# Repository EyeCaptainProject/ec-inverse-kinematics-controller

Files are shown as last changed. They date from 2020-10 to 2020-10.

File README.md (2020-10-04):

# EyeCaptain Mechanical Joystick Controller

This controller can be used to control a joystick if there is no direct digital interface, e.g. to control a wheelchair joystick that has no R-NET or DX-BUS interface. It consists of a 3d-printed part and an Arduino NodeMCU. The mechanical adapter is just mounted on the top of the existing joystick.

## Disclaimer

EyeCaptain does not take any responsibility for the use of the codes and hardware suggestions published here. If you use parts of this project for your own use or for another project, you do so at your own risk. You must check for yourself whether it is a medical device and, if necessary, observe and comply with the guidelines for use and publication applicable in your country. 

# The joystick adapter


We designed a 3D printable mechanical adapter, which can be adjusted in order fit many different joysticks. Two arms are moved by servo motors, which are controlled by an NodeMCU (similar to Arduino Nano, but with WIFI module). The NodeMCU itself is connected to a tablet (via USB or WIFI) and receives the data for direction and speed.

The mechanical adapter consists of four parts:

- 3D printed adapter
- NodeMCU 
- two servo motors (e.g. D-Power DS3218 RC Servo)
- external power supply (necessary because of the quite heavy power consumption of the servo motors)

There are two different ways to connect the NodeMCU to the tablet:
- USB cable
- WIFI

## What is inverse kinematics?

The approach we used in the design is called "inverse kinematics". This means, that the calculation of the coordination at the end of an kinematic line is done backwards. So instead of calculatig the coordinates of the joystick base on the angles of the servo motors, the angles are calculated from the coordinates provided by the devices that delivers x/y positions

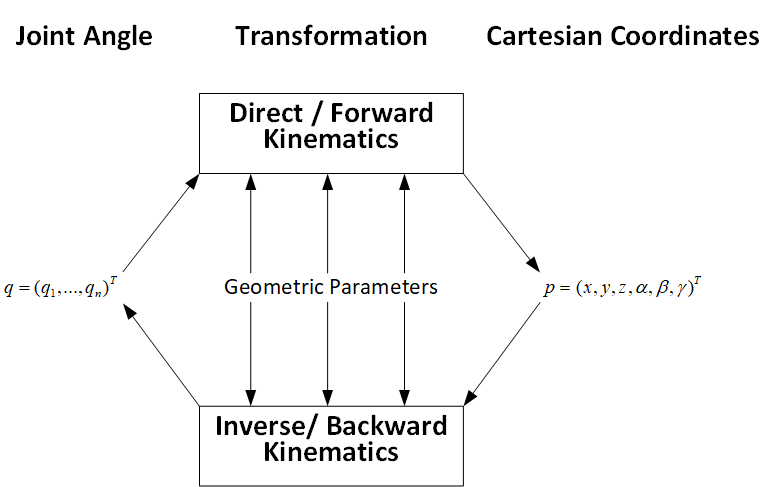
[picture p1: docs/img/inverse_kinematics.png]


The design resembles a 5 bar linkage as shown in the image below, but the horizontal bar a is replaced by the defined position of the servo motors. The two arms in our design consist of the parts "d", "e", "c" and "d", as shown in the image. The blue dot marks the joystick position from a top view and the angles theta1 and theta2 are the angles of the servo motors.

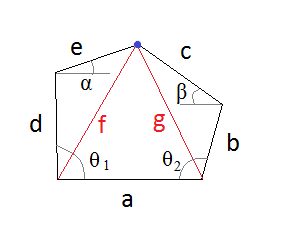
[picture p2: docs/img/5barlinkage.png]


## Steps to build this project

### 1) Print the files in the CAD_Models folder
If you don't have an own 3D printer you may ask the next maker space around you. Very often you find kind people there who are willing to help with printing some parts. 

If you have no idea where the next maker space ist located, you may have a look on this site: [makerspaces.make.co](https://makerspaces.make.co/).

### 2) Assemble all parts (see the images of the assembled model at the top for now, instructions will follow)

### 3) Wire the NodeMCU to the servos and the power supply

The Arduino and the servo motors are connected as depicted in the following image: 

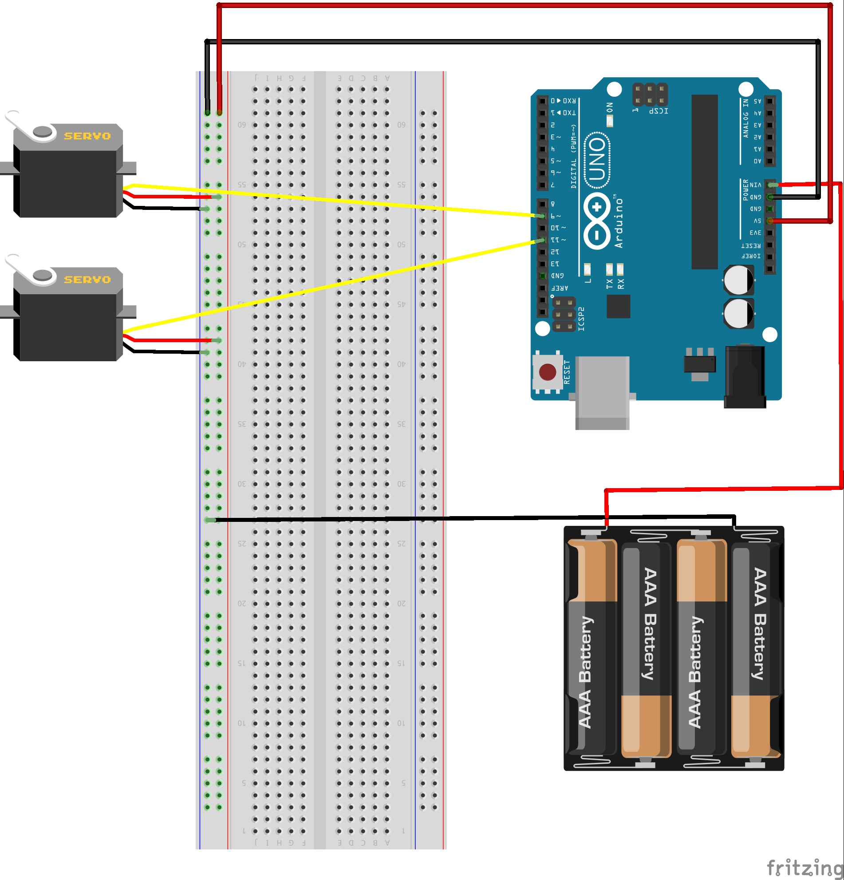
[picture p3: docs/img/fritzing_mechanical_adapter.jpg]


The image above only shows the schematics. For production use, we highly recommend to solder everything to a standard PCB instead of using a breadboard.

### 4) Configure and upload the arduino software to the NodeMCU

- Serial connection is set to `115200` bytes
- The Arduino/NodeMCU software receives X/Y-data (e.g. from a tablet or a phone) and controls the joystick movements with two servo motors and two arms.
- NodeMCU starts a Wifi Hotspot named `EyeCaptain` with the password `EyeCaptain`
- There is a websocket server running on the Ardino device.
- The current implementation of the Arduino-Code also has a webserver with a simple implementation for mobile phones (Folder: `Arduino/data/` that enables you to test the X/Y-position transmission. In order to upload it, you need to use the following Plugin for the Arduino IDE: https://github.com/esp8266/arduino-esp8266fs-plugin. All data that lies in the `Arduino/data` directory will be uploaded to the NodeMcu.
- Once the arduino is running, position data can be sent to either via Websocket-messages or via a Serial Port in the following structure:
```C
%<POSX>,<POSY>;
// e.g.Example:
%50,50;
```
- Position data is between -100/-100 (bottom left) and 100/100 (top right). 0/0 should be the center position
- Files and options that you should configure
    - `Arduino/InverseKinemetics.ino`:
        - Pin configuration
            - `SERVOPINLEFT`: pin of the left servo
            - `SERVOPINRIGHT`: pin of the right servo
        - Adjust the following factors until the servos move exactly 90 degrees
            - `SERVOFAKTORLEFT`: 
            - `SERVOFAKTORRIGHT`:
        - Adjust the NULL-values so that the servo arms are parallel at all times
            - `SERVOLEFTNULL`:  
            - `SERVORIGHTNULL`:
        - You might also need to change the following values:
            - `L1`, `L2`, `L3` (arm length)
            - `O1X`, `O1Y`, `O2X`, `O2Y` (origin point of left and right servo)
        - Parking positions if no data is comin in 
            - `PARKX`
            - `PARKY`        
    - `Arduino/data/websocket.js`: 
        - `IP_ADDRESS` must contain the IP address of the NodeMcU

### 5) Open your browser and connect to the NodeMCU via web iterface

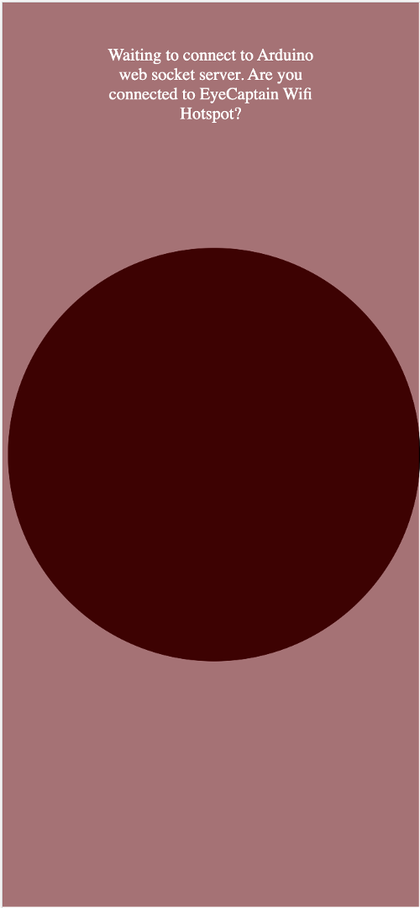
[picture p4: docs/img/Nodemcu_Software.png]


# Explanation of the arduino codes:

- The arduino code in this project is based on the following work of Johannes Heberlein (2014). 
    - https://github.com/9a/plotclock

### Libraries 

Libraries needed:

- https://github.com/Links2004/arduinoWebSockets

```c
#include <ESP8266WiFi.h>
#include <ESP8266WiFiMulti.h>
#include <ArduinoOTA.h>
#include <ESP8266WebServer.h>
#include <ESP8266mDNS.h>
#include <FS.h>
#include <WebSocketsServer.h>
#include <Servo.h>
```

### Calibration

Calibration of servo motor position. Because the lever of the motors are never at the exact same position, it is necessary to calibrate the motors prior to first use in the project.

```c
// Adjust the following factor until the servos move exactly 90 degrees
// D-POWER-servos: 
#define SERVOFAKTORLEFT 700
#define SERVOFAKTORRIGHT 460
// Zero-position of left and right servos
// When in calibration mode, adjust the NULL-values so that the servo arms are at all times parallel
// either to the X or Y axiste
// D-Power servos Werte:
#define SERVOLEFTNULL 2000
#define SERVORIGHTNULL 1050
```

### Geometry factors

The following code describs the geometry of the adapter, which is used for the calculation of the angels (inverse kinematics).

```c
// length of arms
#define L1 35
#define L2 45
#define L3 0 //13.2

// origin points of left and right servo 
#define O1X 40
#define O1Y -25
#define O2X 48
#define O2Y -25
```

### WIFI connection

The nodeMCU sets up an access point for the tablet to log in (WIFI). The name of the network and the passwort are defined in the code.

```c
ESP8266WiFiMulti wifiMulti;       // Create an instance of the ESP8266WiFiMulti class, called 'wifiMulti'

ESP8266WebServer server(80);       // Create a webserver object that listens for HTTP request on port 80
WebSocketsServer webSocket(81);    // create a websocket server on port 81

File fsUploadFile;                 // a File variable to temporarily store the received file

const char *ssid = "EyeCaptain"; // The name of the Wi-Fi network that will be created
const char *password = "EyeCaptain";   // The password required to connect to it, leave blank for an open network

const char *OTAName = "eyecaptain";           // A name and a password for the OTA service
const char *OTAPassword = "eyecaptain";

const char* mdnsName = "eyecaptain"; // Domain name for the mDNS responder
```

### Serial connection

If the NodeMCU is connected to the tablet via WIFI, the serial connection is only for debugging. But you can also use the serial connecting for transmitting the coordinates from the tablet to the Arduino.

```c
Serial.begin(115200);        // Start the Serial communication to send messages to the computer
```

# Overview of the mechanics 3d Parts:

#### Base_Plate.stl
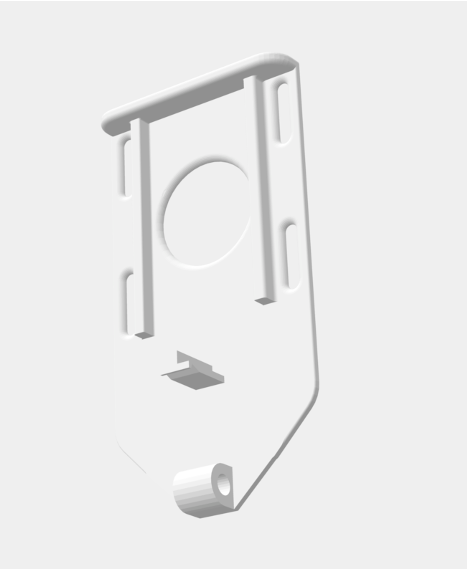
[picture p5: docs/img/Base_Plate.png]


#### Servo_Mount.stl: Holds the two servos
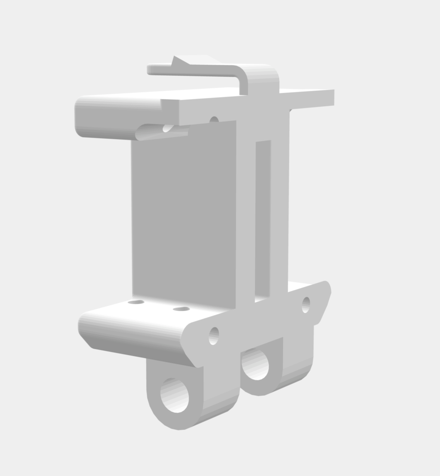
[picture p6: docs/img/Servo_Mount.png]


#### Arm_1.stl
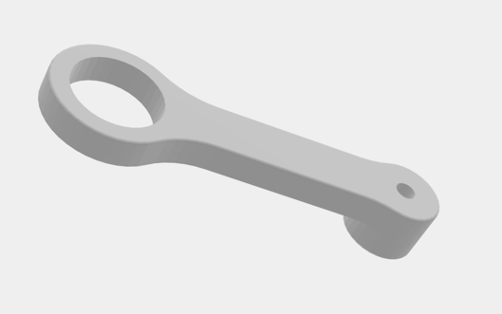
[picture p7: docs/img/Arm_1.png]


#### Arm_2.stl
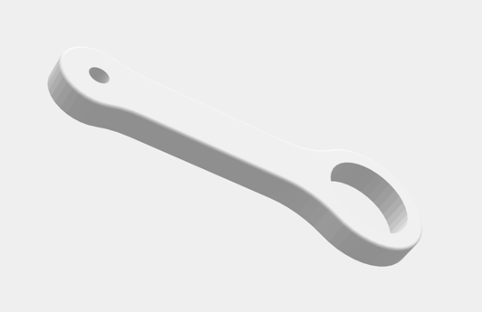
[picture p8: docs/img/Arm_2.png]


#### Arm_Mount_Part1.stl
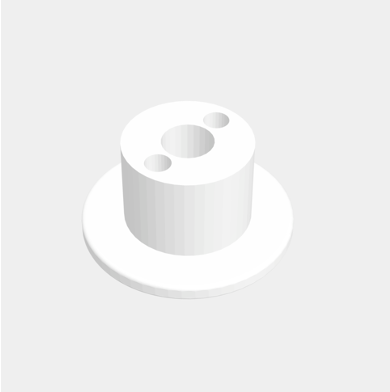
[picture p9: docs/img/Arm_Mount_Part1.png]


#### Arm_Mount_Part2.stl
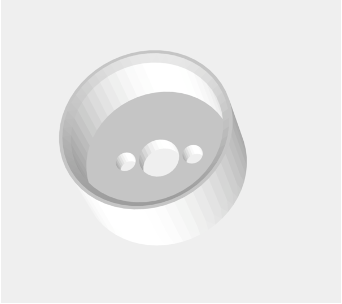
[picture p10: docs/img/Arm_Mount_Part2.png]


#### Simple_Stick.stl
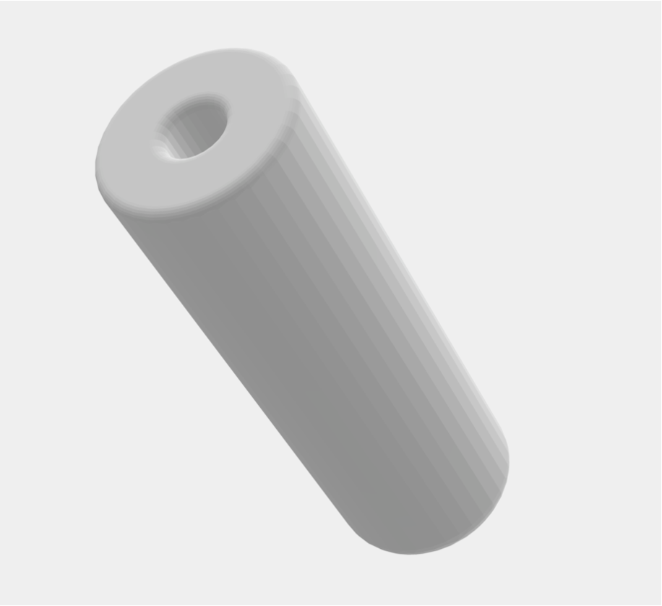
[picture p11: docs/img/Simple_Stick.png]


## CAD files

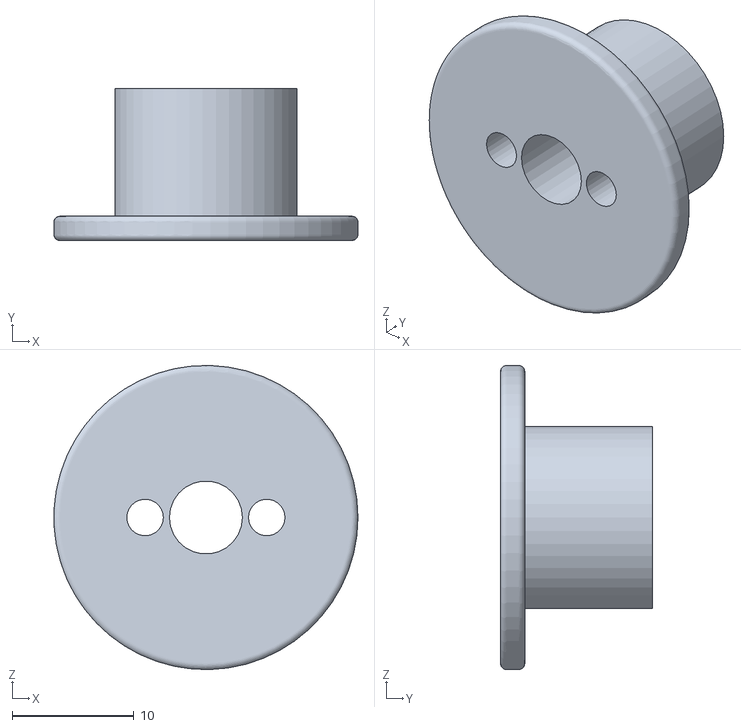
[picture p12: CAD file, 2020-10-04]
CAD_Models/Arm_Mount_Part1.stl
25.0 x 12.5 x 25.0

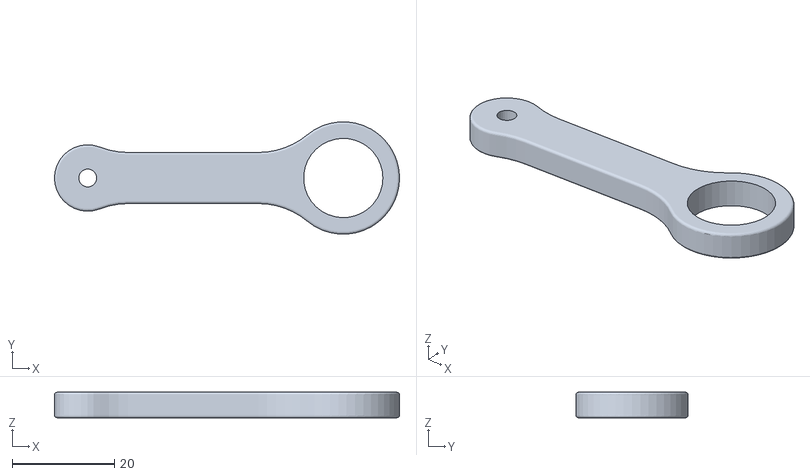
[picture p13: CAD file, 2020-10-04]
CAD_Models/Arm_2.stl
67.5 x 22.0 x 5.00

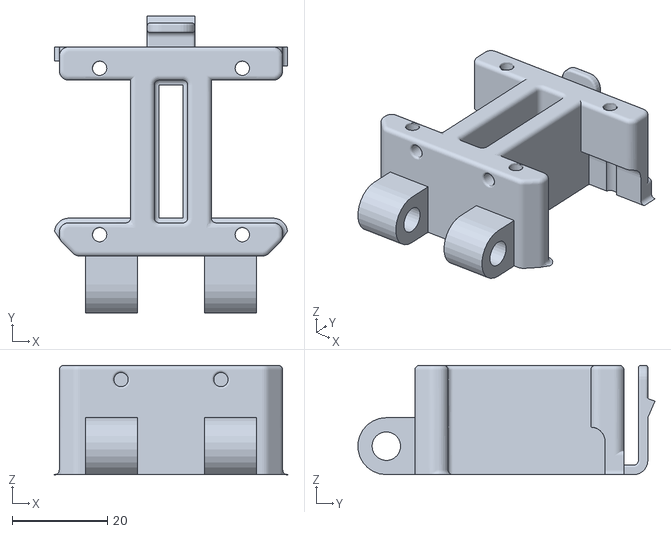
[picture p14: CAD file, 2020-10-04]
CAD_Models/Servo_Mount.stl
49.0 x 62.5 x 23.0

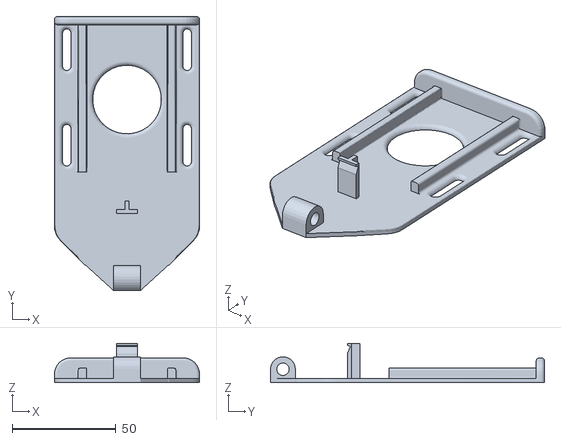
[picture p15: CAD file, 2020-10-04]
CAD_Models/Base_Plate.stl
70.0 x 132.0 x 19.0

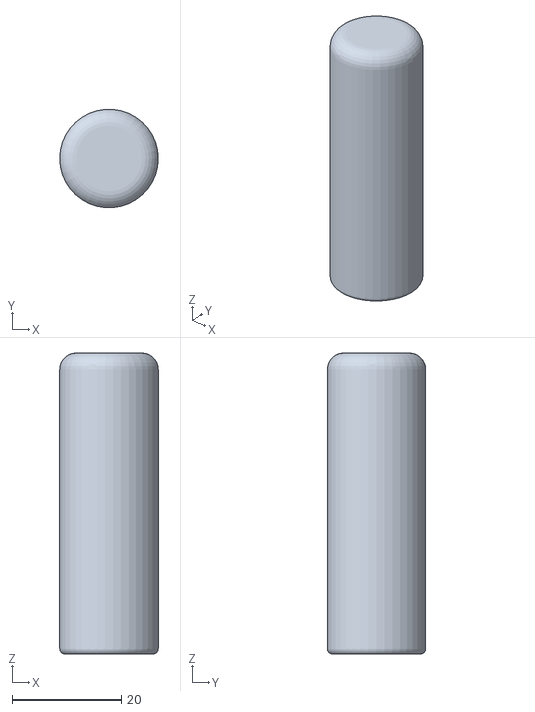
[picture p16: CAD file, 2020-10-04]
CAD_Models/Simple_Stick.stl
18.0 x 17.9 x 55.0

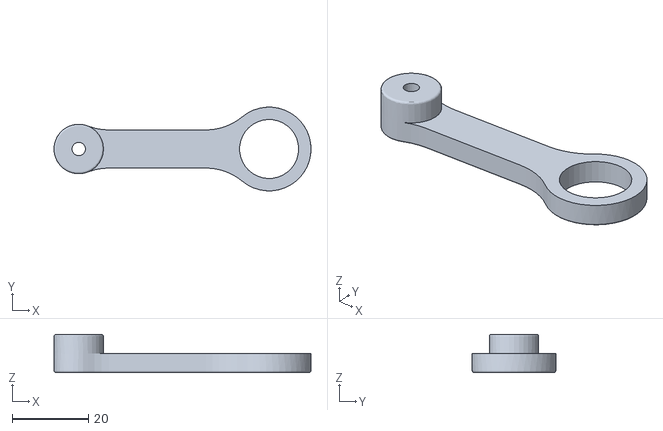
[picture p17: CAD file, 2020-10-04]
CAD_Models/Arm_1.stl
67.5 x 22.0 x 10.0

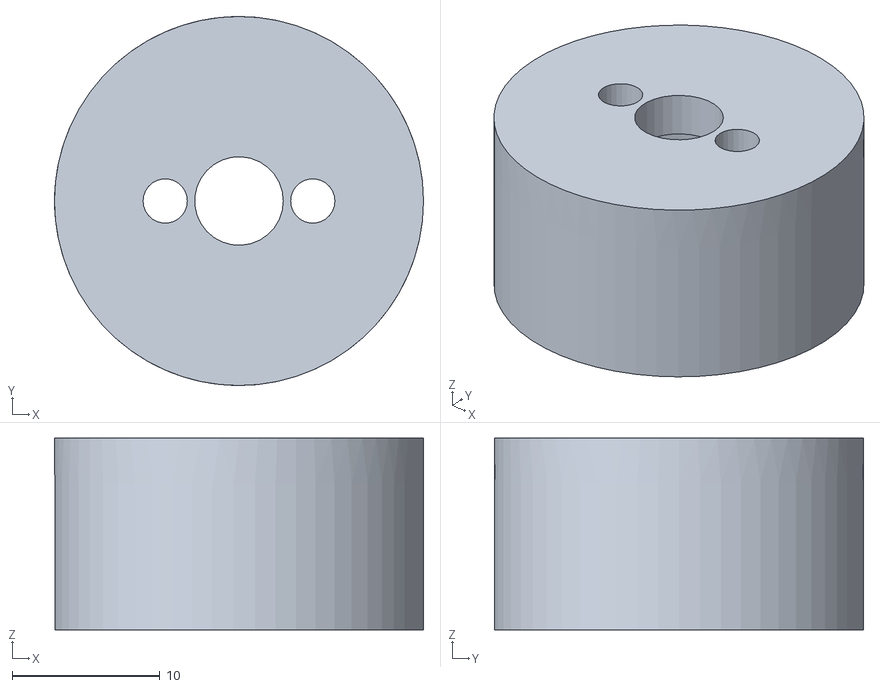
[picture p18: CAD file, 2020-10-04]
CAD_Models/Arm_Mount_Part2.stl
25.0 x 25.0 x 13.0

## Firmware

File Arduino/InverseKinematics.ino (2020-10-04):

#include <ESP8266WiFi.h>
#include <ESP8266WiFiMulti.h>
#include <ArduinoOTA.h>
#include <ESP8266WebServer.h>
#include <ESP8266mDNS.h>
#include <FS.h>
#include <WebSocketsServer.h>
#include <Servo.h>


//Eyecaptain Rollstuhlsteuerung "inverse cinematics"
// units: mm; microseconds; radians

// Adjust the following factor until the servos move exactly 90 degrees
// D-POWER-servos: 
#define SERVOFAKTORLEFT 700
#define SERVOFAKTORRIGHT 460
// Zero-position of left and right servos
// Adapt these values so the arms move parallel to x or y axis
// D-Power servos Werte:
#define SERVOLEFTNULL 2000
#define SERVORIGHTNULL 1050

#define SERVOPINLEFT  D3
#define SERVOPINRIGHT D4

// length of arms
#define L1 35
#define L2 45
#define L3 0 //13.2

// origin points of left and right servo 
#define O1X 40
#define O1Y -25
#define O2X 48
#define O2Y -25

// Parking position of no value coming in 
#define PARKX 33
#define PARKY 33


// Incoming Values between -100 and 100
// Mapped on values between minX/Y and maxX/Y
int xMapped = 0;
int yMapped = 0;
int x;
int y;
int minX = -20;
int maxX = 20;
int minY = -20;
int maxY = 20;

double s2_target = 0;
double s3_target = 0;

Servo servo2;  // 
Servo servo3;  // 

volatile double lastX = PARKX;
volatile double lastY = PARKY;

int last_min = 0;
int driveX=PARKX;
int driveY=PARKY;


ESP8266WiFiMulti wifiMulti;       // Create an instance of the ESP8266WiFiMulti class, called 'wifiMulti'

ESP8266WebServer server(80);       // Create a webserver object that listens for HTTP request on port 80
WebSocketsServer webSocket(81);    // create a websocket server on port 81

File fsUploadFile;                 // a File variable to temporarily store the received file

const char *ssid = "EyeCaptain"; // The name of the Wi-Fi network that will be created
const char *password = "EyeCaptain";   // The password required to connect to it, leave blank for an open network

const char *OTAName = "eyecaptain";           // A name and a password for the OTA service
const char *OTAPassword = "eyecaptain";

const char* mdnsName = "eyecaptain"; // Domain name for the mDNS responder

void setup() {
  
  servo2.attach(SERVOPINLEFT);  //  left servo
  servo3.attach(SERVOPINRIGHT);  //  right servo

  delay(1000);

  Serial.begin(115200);        // Start the Serial communication to send messages to the computer
  delay(10);
  Serial.println("\r\n");

  startWiFi();                 // Start a Wi-Fi access point, and try to connect to some given access points. Then wait for either an AP or STA connection
  
  startOTA();                  // Start the OTA service
  
  startSPIFFS();               // Start the SPIFFS and list all contents

  startWebSocket();            // Start a WebSocket server
  
  startMDNS();                 // Start the mDNS responder

  startServer();               // Start a HTTP server with a file read handler and an upload handler
  
}


unsigned long prevMillis = millis();

int start = 30;
int ende = 50;
int i = start;
int dir = 0;

void loop() {
  webSocket.loop();                           // constantly check for websocket events
  server.handleClient();                      // run the server
  ArduinoOTA.handle();                        // listen for OTA events
  set_XY(driveX,driveY);
      
}


void startWiFi() { // Start a Wi-Fi access point, and try to connect to some given access points. Then wait for either an AP or STA connection
  WiFi.softAP(ssid, password);             // Start the access point
  Serial.print("Access Point \"");
  Serial.print(ssid);
  Serial.println("\" started\r\n");

  Serial.println("\r\n");
  if(WiFi.softAPgetStationNum() == 0) {      // If the ESP is connected to an AP
    Serial.print("Connected to ");
    Serial.println(WiFi.SSID());             // Tell us what network we're connected to
    Serial.print("IP address:\t");
    Serial.print(WiFi.localIP());            // Send the IP address of the ESP8266 to the computer
  } else {                                   // If a station is connected to the ESP SoftAP
    Serial.print("Station connected to ESP8266 AP");
  }
  Serial.println("\r\n");
}

void startOTA() { // Start the OTA service
  ArduinoOTA.setHostname(OTAName);
  ArduinoOTA.setPassword(OTAPassword);

  ArduinoOTA.onStart([]() {
    Serial.println("Start");
  });
  ArduinoOTA.onEnd([]() {
    Serial.println("\r\nEnd");
  });
  ArduinoOTA.onProgress([](unsigned int progress, unsigned int total) {
    Serial.printf("Progress: %u%%\r", (progress / (total / 100)));
  });
  ArduinoOTA.onError([](ota_error_t error) {
    Serial.printf("Error[%u]: ", error);
    if (error == OTA_AUTH_ERROR) Serial.println("Auth Failed");
    else if (error == OTA_BEGIN_ERROR) Serial.println("Begin Failed");
    else if (error == OTA_CONNECT_ERROR) Serial.println("Connect Failed");
    else if (error == OTA_RECEIVE_ERROR) Serial.println("Receive Failed");
    else if (error == OTA_END_ERROR) Serial.println("End Failed");
  });
  ArduinoOTA.begin();
  Serial.println("OTA ready\r\n");
}

void startSPIFFS() { // Start the SPIFFS and list all contents
  SPIFFS.begin();                             // Start the SPI Flash File System (SPIFFS)
  Serial.println("SPIFFS started. Contents:");
  {
    Dir dir = SPIFFS.openDir("/");
    while (dir.next()) {                      // List the file system contents
      String fileName = dir.fileName();
      size_t fileSize = dir.fileSize();
      //Serial.printf("\tFS File: %s, size: %s\r\n", fileName.c_str(), formatBytes(fileSize).c_str());
    }
    Serial.printf("\n");
  }
}

void startWebSocket() { // Start a WebSocket server
  webSocket.begin();                          // start the websocket server
  webSocket.onEvent(webSocketEvent);          // if there's an incomming websocket message, go to function 'webSocketEvent'
  Serial.println("WebSocket server started.");
}

void startMDNS() { // Start the mDNS responder
  MDNS.begin(mdnsName);                        // start the multicast domain name server
  Serial.print("mDNS responder started: http://");
  Serial.print(mdnsName);
  Serial.println(".local");
}

void startServer() { // Start a HTTP server with a file read handler and an upload handler
  server.on("/edit.html",  HTTP_POST, []() {  // If a POST request is sent to the /edit.html address,
    server.send(200, "text/plain", ""); 
  }, handleFileUpload);                       // go to 'handleFileUpload'

  server.onNotFound(handleNotFound);          // if someone requests any other file or page, go to function 'handleNotFound'
                                              // and check if the file exists

  server.begin();                             // start the HTTP server
  Serial.println("HTTP server started.");
}


void webSocketEvent(uint8_t num, WStype_t type, uint8_t * payload, size_t lenght) { // When a WebSocket message is received
  driveX = PARKX;
  driveY = PARKY;
  switch (type) {
    case WStype_DISCONNECTED:             // if the websocket is disconnected
      Serial.printf("[%u] Disconnected!\n", num);
      break;
    case WStype_CONNECTED: {              // if a new websocket connection is established
        IPAddress ip = webSocket.remoteIP(num);
        Serial.printf("[%u] Connected from %d.%d.%d.%d url: %s\n", num, ip[0], ip[1], ip[2], ip[3], payload);
      }
      break;
    case WStype_TEXT:                     // if new text data is received
      //Serial.printf("[%u] get Text: %s\n", num, payload);
      String str = (char*)payload;
      int codePos = str.indexOf("%");
      int commaPos = str.indexOf(",");
      int strichpktPos = str.indexOf(";");
      if(codePos == -1 || commaPos == -1 || strichpktPos == -1) {
        // void
      }else{
        // needs to be the length of identifier
        String x_str = str.substring(1, commaPos);
        String y_str = str.substring(commaPos+1,strichpktPos);
        char floatbuf_x[64]; // mindestens 64 bit großen Buffer erzeugen
        char floatbuf_y[64]; 
        x_str.toCharArray(floatbuf_x, sizeof(floatbuf_x)); // In Buffer laden
        y_str.toCharArray(floatbuf_y, sizeof(floatbuf_y));
        x = atof(floatbuf_x); 
        y = atof(floatbuf_y);
  
        // SERVO_MAPPING muss nicht zwischen < und > 0 unterscheiden:
        xMapped = map(x, -100, 100, minX, maxX);
        yMapped = map(y, -100, 100, minY, maxY);
        driveX = PARKX+xMapped;
        driveY = PARKY+yMapped;  
      }
      
    break;
  }
}

// Writing numeral with bx by being the bottom left originpoint. Scale 1 equals a 20 mm high font.
// The structure follows this principle: move to first startpoint of the numeral, lift down, draw numeral, lift up
double return_angle(double a, double b, double c) {
  // cosine rule for angle between c and a
  return acos((a * a + c * c - b * b) / (2 * a * c));
}

void set_XY(double Tx, double Ty) 
{
  delay(1);
  double dx, dy, c, a1, a2, Hx, Hy;

  // calculate triangle between pen, servoLeft and arm joint
  // cartesian dx/dy
  dx = Tx - O1X;
  dy = Ty - O1Y;

  // polar lemgth (c) and angle (a1)
  c = sqrt(dx * dx + dy * dy); // 
  a1 = atan2(dy, dx); //
  a2 = return_angle(L1, L2, c);

  

  // calculate joinr arm point for triangle of the right servo arm
  double a2_2 = return_angle(L2, L1, c);
  Hx = Tx + L3 * cos((a1 - a2_2 + 0.621) + M_PI); //36,5°
  Hy = Ty + L3 * sin((a1 - a2_2 + 0.621) + M_PI);

  // calculate triangle between pen joint, servoRight and arm joint
  dx = Hx - O2X;
  dy = Hy - O2Y;

  c = sqrt(dx * dx + dy * dy);
  double a1_2 = atan2(dy, dx);
  a2_2 = return_angle(L1, (L2 - L3), c);


 s2_target = floor(((a1_2 - a2_2) * SERVOFAKTORRIGHT) + SERVORIGHTNULL);
 s3_target = floor(((a2 + a1 - M_PI) * SERVOFAKTORLEFT) + SERVOLEFTNULL);


servo2.writeMicroseconds(s2_target);
servo3.writeMicroseconds(s3_target);

}




void handleNotFound(){ // if the requested file or page doesn't exist, return a 404 not found error
  if(!handleFileRead(server.uri())){          // check if the file exists in the flash memory (SPIFFS), if so, send it
    server.send(404, "text/plain", "404: File Not Found");
  }
}

bool handleFileRead(String path) { // send the right file to the client (if it exists)
  Serial.println("handleFileRead: " + path);
  if (path.endsWith("/")) path += "index.html";          // If a folder is requested, send the index file
  String contentType = getContentType(path);             // Get the MIME type
  String pathWithGz = path + ".gz";
  if (SPIFFS.exists(pathWithGz) || SPIFFS.exists(path)) { // If the file exists, either as a compressed archive, or normal
    if (SPIFFS.exists(pathWithGz))                         // If there's a compressed version available
      path += ".gz";                                         // Use the compressed verion
    File file = SPIFFS.open(path, "r");                    // Open the file
    size_t sent = server.streamFile(file, contentType);    // Send it to the client
    file.close();                                          // Close the file again
    Serial.println(String("\tSent file: ") + path);
    return true;
  }
  Serial.println(String("\tFile Not Found: ") + path);   // If the file doesn't exist, return false
  return false;
}
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
